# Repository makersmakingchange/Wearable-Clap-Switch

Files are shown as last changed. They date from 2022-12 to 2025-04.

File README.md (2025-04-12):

# Wearable Clap Switch

The Wearable Clap Switch is a wireless assistive switch designed for users that have difficulty using traditional pressure based switches. It consists of a hand mounted transmitter, and a receiver box. When the transmitter detects a clap motion, it sends a signal to the receiver which activates the mono jack. The receiver can be used to activate an 3.5 mm assistive device like a switch adapted toy.

The original version of this project is called the Wearable Bluetooth Controller for Switch Adapted Toys. It was released by [r570sv](https://www.instructables.com/member/r570sv/) on [Instructables](https://www.instructables.com/Wearable-BLE-Controller-for-Switch-Adapted-Toys/) under a [CC-BY-NC-SA license](https://creativecommons.org/licenses/by-nc-sa/4.0/).

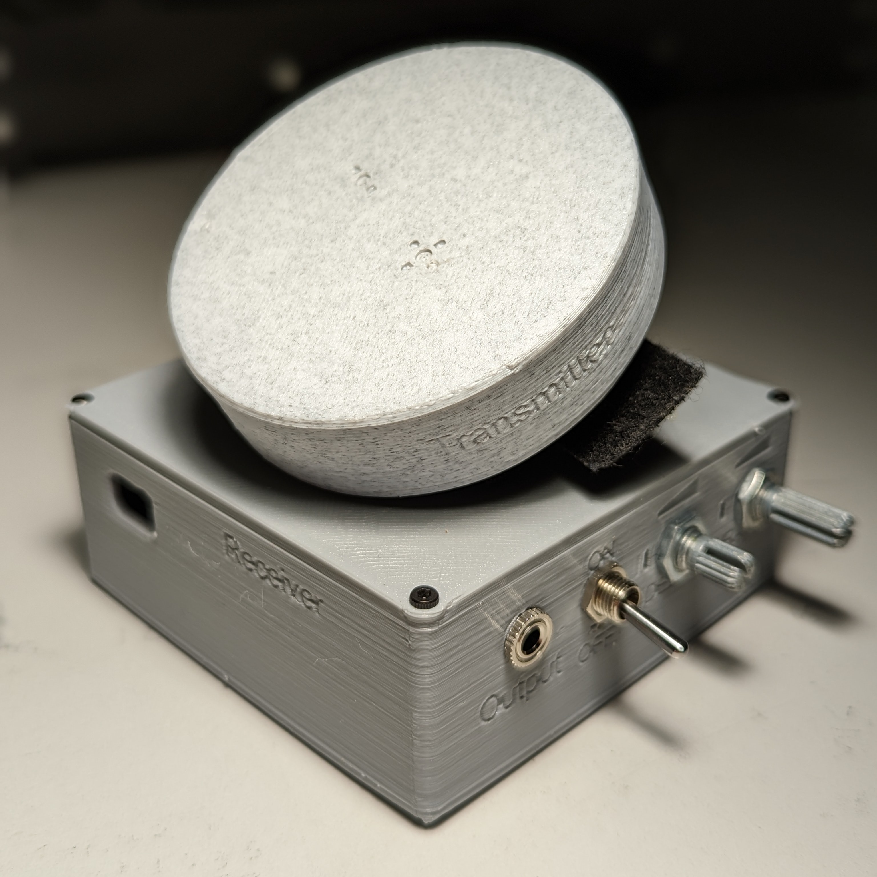
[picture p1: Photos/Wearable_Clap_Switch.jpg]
Picture of Wearable Clap Switch.


## More info at
- [Makers Making Change Project Page](https://makersmakingchange.com/project/wearable-clap-switch)

## How to Obtain a Wearable Clap Switch
### 1. Do it Yourself (DIY) or Do it Together (DIT)

This is an open-source assistive technology, so anyone is free to build it. All of the files and instructions required to build the Wearable Clap Switch are contained within this repository. Refer to the Maker Checklist below.

### 2. Request a build of this device

If you would like to obtain a Wearable Clap Switch , you may submit a build request through the [MMC Library Page](https://makersmakingchange.com/project/wearable-clap-switch/). The requestor is responsible for the cost of materials and any shipping.

### 3. How to build this device for someone else

If you have the skills and equipment to build this device, and would like to donate your time to create the switch for someone who needs it, visit the [MMC Maker Wanted](https://makersmakingchange.com/maker-wanted/) section.

## Getting Started

### 1. Read the Makers Checklist

The Makers Checklist contains all the steps required to build the device for someone.

### 2. Order the Off-The-Shelf Components

The [Bill of Materials](/Documentation/Wearable_Clap_Switch_BOM.xlsx) lists all of the parts and components required to build the Wearable Clap Switch. The main switch component needs to be ordered online. The rest of the off-the-shelf components are also online or may be available in smaller quantities at your local hardware store or dollar store.

### 3. Print the 3D Printable components

Print the components. All of the files and individual print files can be in the [/Build_Files/3D_Printing_Files](/Build_Files/3D_Printing_Files/) folder.

### 4. Assemble the Wearable Clap Switch

Reference the [Assembly Guide](/Documentation/Wearable_Clap_Switch_Assembly_Guide_V1.0.pdf) for the tools and steps required to build each portion.

## Files
### Documentation
| Document             | Version | Link |
|----------------------|---------|------|
| Design Rationale     | 1.0     | [Wearable_Clap_Switch_Design_Rationale](/Documentation/Wearable_Clap_Switch_Design_Rationale_v1.0.pdf)     |
| Maker Checklist      | 1.0     | [Wearable_Clap_Switch_Maker_Checklist](/Documentation/Wearable_Clap_Switch_Maker_Checklist_v1.0.pdf)     |
| Bill of Materials    | 1.0     | [Wearable_Clap_Switch_Bill_of_Materials](/Documentation/Wearable_Clap_Switch_BOM_v1.0.xlsx)     |
| 3D Printing Guide    | 1.0     | [Wearable_Clap_Switch_3D_Printing_Guide](/Documentation/Wearable_Clap_Switch_3D_Printing_Guide_v1.0.pdf)     |
| Assembly Guide       | 1.0     | [Wearable_Clap_Switch_Assembly_Guide](/Documentation/Wearable_Clap_Switch_Assembly_Guide_v1.0.pdf)     |
| User Guide           | 1.0     | [Wearable_Clap_Switch_User_Guide](/Documentation/Wearable_Clap_Switch_User_Guide_v1.0.pdf)    |
| Changelog            | 1.0     | [Wearable_Clap_Switch_Changelog](/Documentation/Wearable_Clap_Switch_Changelog_v1.0.pdf)     |

### Design Files
 - [CAD Files](/Build_Files/Design_Files)

### Build Files
 - [3D Printing Files](/Build_Files/3D_Printing)

### Programming Files
 - [Programming Files](/Code/Current_Code)

## Attribution
The original design of the [Wearable Bluetooth Controller for Switch Adapted Toys](https://www.instructables.com/Wearable-BLE-Controller-for-Switch-Adapted-Toys/) was released by [r570sv](https://www.instructables.com/member/r570sv/) under a [CC-BY-NC-SA license](https://creativecommons.org/licenses/by-nc-sa/4.0/).

Updated 3D Printed Receiver Design, code, and documentation by Brad Wellington / Makers Making Change.

## License
Everything needed or used to design, make, test, or prepare the Wearable Clap Switch is licensed under the [Creative Commons Attribution-NonCommercial-ShareAlike 4.0](https://creativecommons.org/licenses/by-nc-sa/4.0/) . 

Accompanying material such as instruction manuals, videos, and other copyrightable works that are useful but not necessary to design, make, test, or prepare the Wearable Clap Switch are published under a Creative Commons Attribution-ShareAlike 4.0 license https://creativecommons.org/licenses/by-sa/4.0/ (CC BY-SA 4.0).

---
<!-- ABOUT MMC START -->
## About Makers Making Change
[Makers Making Change Logo](https://www.makersmakingchange.com/)

Makers Making Change is a program of [Neil Squire](https://www.neilsquire.ca/), a Canadian non-profit that uses technology, knowledge, and passion to empower people with disabilities.

Makers Making Change leverages the capacity of community based Makers, Disability Professionals and Volunteers to develop and deliver affordable Open Source Assistive Technologies.

 - Website: [www.MakersMakingChange.com](https://www.makersmakingchange.com/)
 - GitHub: [makersmakingchange](https://github.com/makersmakingchange)
 - Bluesky: [@makersmakingchange.bsky.social](https://bsky.app/profile/makersmakingchange.bsky.social)
 - Instagram: [@makersmakingchange](https://www.instagram.com/makersmakingchange)
 - Facebook: [makersmakechange](https://www.facebook.com/makersmakechange)
 - LinkedIn: [Neil Squire Society](https://www.linkedin.com/company/neil-squire-society/)
 - Thingiverse: [makersmakingchange](https://www.thingiverse.com/makersmakingchange/about)
 - Printables: [MakersMakingChange](https://www.printables.com/@MakersMakingChange)

### Contact Us
For technical questions, to get involved, or to share your experience we encourage you to [visit our website](https://www.makersmakingchange.com/) or [contact us](https://www.makersmakingchange.com/s/contact).
<!-- ABOUT MMC END -->

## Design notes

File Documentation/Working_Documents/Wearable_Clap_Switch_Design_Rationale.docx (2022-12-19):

# Introduction

The Wearable Clap Switch is a device that operates a switch when the user claps. It is intended for users that have difficulty operating standard push or squeeze switches.

# Research

Commercial Options
Name | Picture | Price | Link

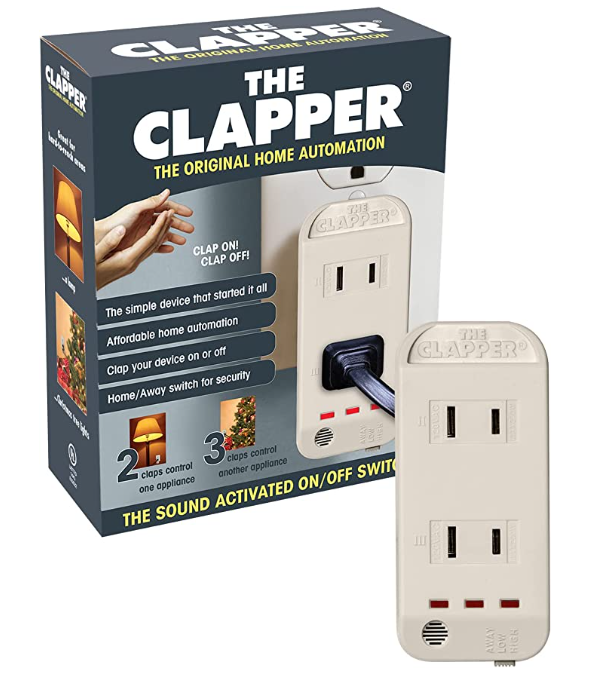
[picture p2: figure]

Clapper Activated Sound Switch | | $39.15 | Link (https://www.amazon.ca/Clapper-Sound-Activated-Switch-Each/dp/B0000CGKLR)

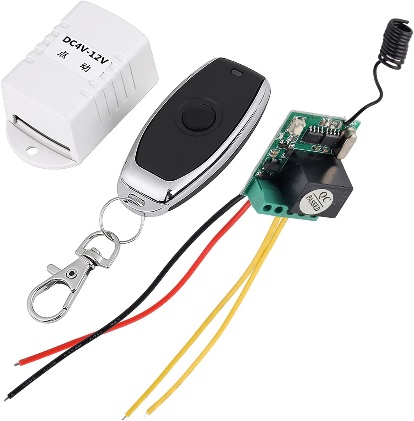
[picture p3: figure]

Wireless Switch Receiver | | $19.02 | Link (https://www.amazon.ca/gp/product/B0762HH45G/ref=ppx_yo_dt_b_asin_title_o01_s00?ie=UTF8&psc=1)

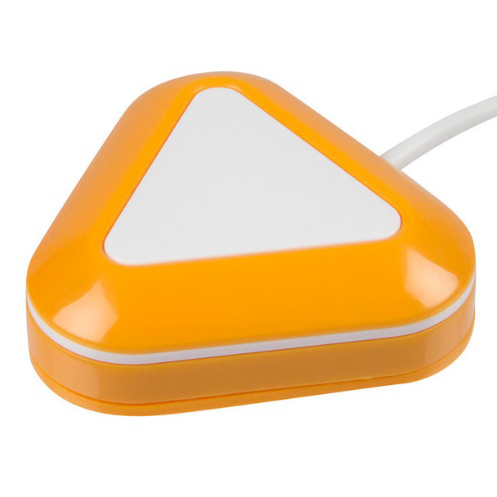
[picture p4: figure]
LITTLE Candy Corn Proximity Switch

Little Candy Corn Proximity Switch | | $310.14 | Link (https://www.adaptivetechsolutions.com/little-candy-corn-proximity-switch/)

DIY Options

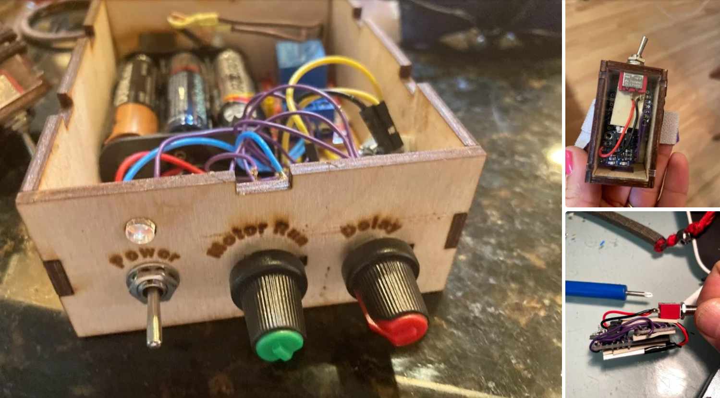
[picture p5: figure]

Wearable Bluetooth Controller for Switch Adapted Toys | | | Link (https://www.instructables.com/Wearable-BLE-Controller-for-Switch-Adapted-Toys/)

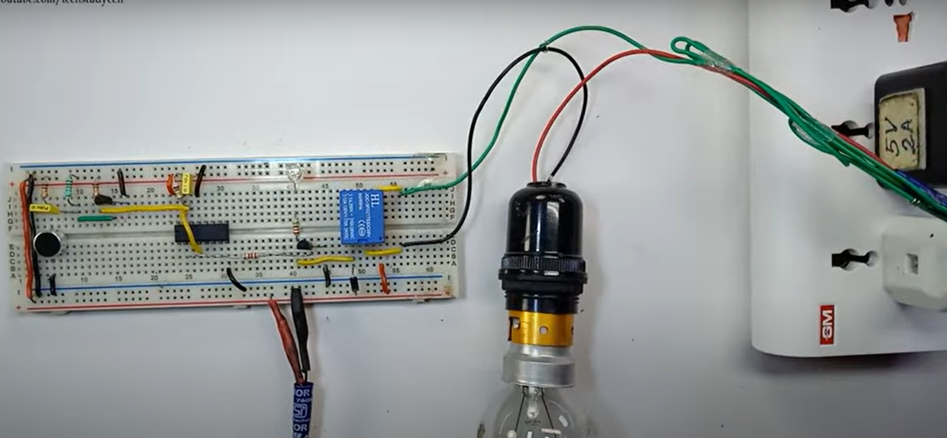
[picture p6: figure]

Simple Clap Circuit for Home Automation | | | Link (https://www.youtube.com/watch?v=KToo8p2EG-4)

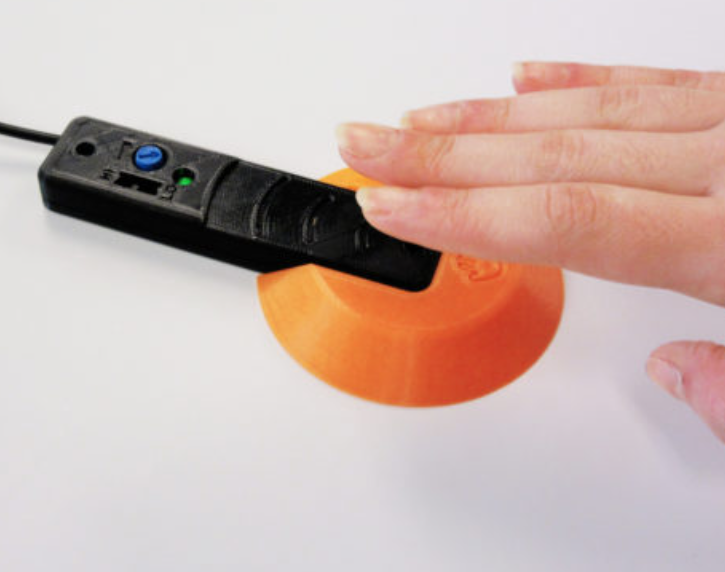
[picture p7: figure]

Light Proximity Switch | | | Link (https://makersmakingchange.com/project/light-proximity-switch/)

# Requirements

## Goals

G01 | Operate a switch when the user claps

## Functional Requirements

F01 | Device must operate a switch when the user claps(or just accelerates their hand?)
F02 | Device must not hinder/obstruct user (e.g. tangle them with wires)
F03 | Device must have adjustable switch delay and duration
F04 | Device must have a 3.5 mm mono output port.
F05 | Device must be chargeable/easy to change batteries.

## Non-functional Requirement

NF01 | All Parts must be off the shelf/3D printable
NF02 | Maker Friendly/Easy to assemble
NF03 | Any handheld/strapped parts of the device must be comfortable enough to wear for long periods of time

## Constraints

C01 | Low-Cost

# Ideation

The idea for this project came from the original instructable project, which designed a clap-based switch for a person who had difficulty interacting with push or squeeze based switches but was very good at clapping.

## User Controllable Parameters

- Duration of the output
- Delay between activations
- Triggering sensitivity (i.e., accelerometer threshold)

## Trigger Method

- Original – acceleration magnitude
- Gesture recognition
- Sounds intensity threshold

# Conceptual Design

## Original Design

This design stays true to the original Instructables design, using two ItsyBitsy nrf52840 microcontrollers, full size potentiometers, and soldered Dupont wires.

The device consists of one handheld unit containing an accelerometer and a Bluetooth microcontroller. When the microcontroller detects movement over a threshold, it sends a signal to the receiver unit. The receiver unit contains another Bluetooth microcontroller, a relay, two input potentiometers, and a 3.5 mm mono jack. When the receiver gets the signal, it activates the relay to close the output jack with a delay and duration set by the input potentiometers.

~$100-$110

### Opportunities for Improvement

- Find alternative relay board to reduce BOM cost

## Concept 2 – Different Microcontroller

This concept is similar to the original design, but switches to Feather microcontrollers. This brings the battery backpacks onto the main board and allows for Featherwing boards to be used to bring the amount of soldering and loose wires to a minimum. There are several relay Featherwings, with both regular and solid state relays, as well as several accelerometer Featherwings.

The device consists of one handheld unit containing an accelerometer and a Bluetooth microcontroller. When the microcontroller detects movement over a threshold, it sends a signal to the receiver unit. The receiver unit contains another Bluetooth microcontroller, a relay, two input potentiometers, and a 3.5 mm mono jack. When the receiver gets the signal, it activates the relay to close the output jack with a delay and duration set by the input potentiometers.

~$130-$140

## Concept 3 – Wireless Relay Switch

This concept uses the same wireless relay switch as the Wireless Assistive Switch Link (https://makersmakingchange.com/project/wireless-assistive-switch-link/) project with a small microcontroller such as the Seed Xiao SAMD21 connected to the accelerometer in the hand mounted enclosure. When the accelerometer detects a movement over the threshold, it signals the transmitter with a duration and delay set by the two input potentiometers on the handheld unit. When the receiver relay gets a signal, it will send a signal to the 3.5 mm mono output port as long as it continues to receive the input signal.

The primary downside of this concept is the fact that the duration and delay potentiometers have to be mounted on the hand section of the device to control the output to the wireless relay switch. This is added weight, but there are small potentiometers that can be used, such as the ones on the OpenAT Toy

~$50-$60

## Concept 4 – Clapper

This concept consists of a base station connected to the switch that monitors for the sound of a clap, and will activate the switch when a clap is picked up by a microphone. The switch is activated with a relay which is connected to a 3.5 mm mono output jack with a delay and duration set by two input potentiometers.

~$35-$45

## Concept 5 – Microcontroller with Integrated Sensor

This design is similar to the original design but swaps the hand mounted microcontroller for a board with an onboard accelerometer, Bluetooth, and battery management such as the Feather nrf52840 Sense or the Circuit Playground Bluefruit. These microcontrollers typically have a microphone on board as well, which would allow for verification of a clap through both acceleration and sound.

The device consists of one handheld unit containing a Bluetooth microcontroller with built in accelerometer and microphone. When the microcontroller detects movement over a threshold and confirms the clap with sound from the microphone, it sends a signal to the receiver unit. The receiver unit contains another Bluetooth microcontroller, a relay, two input potentiometers, and a 3.5 mm mono jack. When the receiver gets the signal, it activates the relay to close the output jack with a delay and duration set by the input potentiometers.

~$100-$110

## Concept Comparison

Criteria/Concept | Original | Concept 2 | Concept 3 | Concept 4 | Concept 5
Function | 7 | 7 | 7 | 6 | 8
Battery Life | N/A | N/A | N/A | N/A | N/A
Size | 4 | 6 | 8 | 7 | 8
Weight | 5 | 6 | 7 | 9 | 7
Price | 7 | 6 | 8 | 9 | 6
Adaptability | 6 | | | | 9
Customizability | 6 | 6 | 4 | 3 | 9
Makeability | 6 | 7 | 6 | 5 | 8
Design Effort | 7 | 7 | 6 | 6 | 7

# Detailed Design

## Power Supply Options

- LiPo Battery Pack
  - ~3.7 V DC
  - No power switch
  - Would need to be able to access the JST connector to charge the battery
  - Difficult to ship
  - ~150 mAh, can increase to up to 2000 mAh with enclosure redesign
  - ~5 to 66.5 h of battery life
  - With very minimal enclosure changes, 350 mAh battery can be installer with ~11.5h battery life
  - Charge rate of 100 mA
- AAA battery pack
  - 3xAAA batteries, ~4.5 V DC
  - Power switch
  - Would need to disassemble to change batteries
  - ~1200 mAh
  - As thick as the current enclosure
  - ~40h of battery life
- Coin cell
  - 2xCR2032 ~6 V DC
  - Power switch
  - Would need to disassemble to change batteries
  - ~235 mAh
  - ~7.5h of battery life

Circuit playground can take up to 6V DC and has reverse polarity, over-current, and thermal protection. The circuit playground consumes around 30 mA of current during operation. (https://blog.adafruit.com/2019/10/25/circuitplayground-bluefruit-low-power-tests-adafruit-bluefruit-arduino-circuitpython/)

## Enclosure Design

### Transmitter

- Lightweight
- Charging port accessible
- No sharp edges

### Receiver

- Charging port accessible
- No sharp edges

# Opportunities for Improvement

Transmitter

- Integrate charging circuit into the enclosure
- Change the communication protocol so the transmitter can be used for more projects, like controlling a remote-control car.
- Stiffen base so it won’t warp if removed from print bed while warm

Receiver

- Add knobs on input potentiometers
- Cover on programming port

© 2022 by Neil Squire. This work is licensed under the CC BY SA 4.0 License: http://creativecommons.org/licenses/by-sa/4.0 Files available at https://makersmakingchange.com/project/wearable-clap-switch/ Page 1 of 2

V1.0 | December 2022 Wearable Clap Switch Design Rationale

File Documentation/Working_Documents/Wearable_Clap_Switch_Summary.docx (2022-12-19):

# Title

Wearable Clap Switch

## Subtitle

The Wearable Clap Switch allows a user to wirelessly activate a switch activated device with a clap.

## Device Details

### Overview

The Wearable Clap Switch is a wireless assistive switch designed for users that have difficulty using traditional pressure based switches. It consists of a hand mounted transmitter, and a receiver box. When the transmitter detects a clap motion, it sends a signal to the receiver which activates the mono jack. The receiver can be used to activate an 3.5 mm assistive device like a switch adapted toy.

The original version of this project is called the Wearable Bluetooth Controller for Switch Adapted Toys. It was released by r570sv (https://www.instructables.com/member/r570sv/) on Instructables (https://www.instructables.com/Wearable-BLE-Controller-for-Switch-Adapted-Toys/) under a CC-BY-NC-SA (https://creativecommons.org/licenses/by-nc-sa/4.0/) license.

### Usage

When a clap motion is detected by the hand-mounted transmitter, the receiver will activate the connected assistive device.

Transmitter

Attach the transmitter to the users hand or wrist using the strap.

To activate the transmitter, slide the switch on the bottom of the transmitter. The transmitter will start looking for a connection, and if a receiver is broadcasting, the two will connect. Once the two have connected, the transmitter will send a signal to the receiver whenever it detects a clap.

The sensitivity of the clap detection can be adjusted using the two buttons on the top of the case. Pressing the increase sensitivity button will cause the number of illuminated LEDs in the circle to increase. Pressing the decrease sensitivity button will cause the number of illuminated LEDs in the circle to decrease.

Receiver

Connect the assistive device to the output port on the receiver using a 3.5 mm cable.

To active the receiver, flip the toggle switch from off to on. The receiver will start looking for a connection, and if the transmitter is broadcasting, the two will connect. Once they have connected, the receiver will power a relay to activate the mono jack.

To change how long the jack stays activated, adjust the potentiometer labeled Duration. To change the cooldown between activations, adjust the potentiometer labeled Delay.

### Cost

~$110

### Build Instructions

The transmitter is assembled with mostly off the shelf parts, the only addition being the soldering of a power switch onto the battery line. All the shell and other mechanical components are 3D printed. For the receiver, there is medium soldering to assemble the protoboard

#### Skills Required

- 3D Printing
- Soldering

#### Time Required

- 3D Print Time: 12h 8min
- Assembly Time: 1h

#### Tools

- 3D printer
- Soldering iron
- Hobby knife
- Multimeter
- Flush cutters
- Flux

#### Components

- 1X Transmitter
- 1X Receiver

#### 3D Printing

All components can be printed with no support at 20% infill with a 0.2mm layer height. All pieces can be printed using PLA filament Programming

### Attribution

The original design of the Wearable Bluetooth Controller for Switch Adapted Toys (https://www.instructables.com/Wearable-BLE-Controller-for-Switch-Adapted-Toys/) was released by r570sv (https://www.instructables.com/member/r570sv/) under a CC-BY-NC-SA (https://creativecommons.org/licenses/by-nc-sa/4.0/) license.

Updated 3D Printed Receiver Design, code, and documentation by Brad Wellington / Makers Making Change.

© 2022 by Neil Squire. This work is licensed under the CC BY SA 4.0 License: http://creativecommons.org/licenses/by-sa/4.0 Files available at https://makersmakingchange.com/project/wearable-clap-switch/ Page 2 of 3

V1.0 | December 2022 Wearable Clap Switch Summary

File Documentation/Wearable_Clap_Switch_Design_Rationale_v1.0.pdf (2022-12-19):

V1.0 | December 2022

## Wearable Clap Switch

## DESIGN RATIONALE

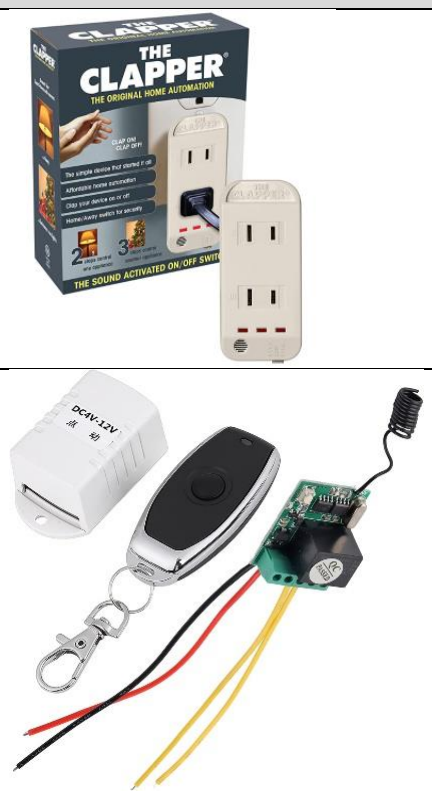
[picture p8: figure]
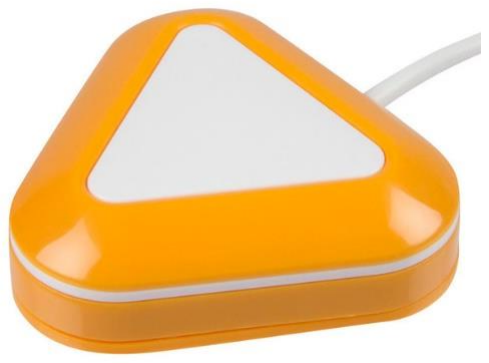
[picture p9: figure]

© 2022 by Neil Squire. (https://neilsquire.ca/)
This work is licensed under the CC BY SA 4.0 License: http://creativecommons.org/licenses/by-sa/4.0
Files available at https://makersmakingchange.com/project/wearable-clap-switch/ (https://makersmakingchange.com/?post_type=project&p=20045&preview=true) | Page 1 of 7

### Introduction

The Wearable Clap Switch is a device that operates a switch when the user claps. It is intended for users that have difficulty operating standard push or squeeze switches.

### Research

Commercial Options
Name | Picture | Price | Link
Clapper Activated Sound Switch | | $39.15 | Link (https://www.amazon.ca/Clapper-Sound-Activated-Switch-Each/dp/B0000CGKLR)
Wireless Switch Receiver | | $19.02 | Link (https://www.amazon.ca/gp/product/B0762HH45G/ref=ppx_yo_dt_b_asin_title_o01_s00?ie=UTF8&psc=1)
Little Candy Corn Proximity Switch | | $310.14 | Link (https://www.adaptivetechsolutions.com/little-candy-corn-proximity-switch/)

## DESIGN RATIONALE

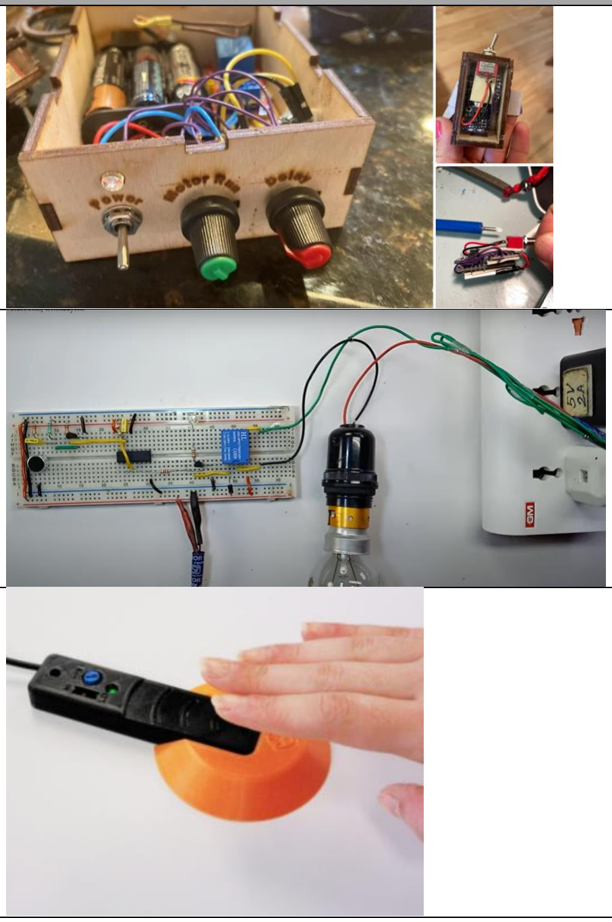
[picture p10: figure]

Files available at https://makersmakingchange.com/project/wearable-clap-switch/ (https://makersmakingchange.com/?post_type=project&p=20045&preview=true) | Page 2 of 7

DIY Options
Wearable Bluetooth Controller for Switch Adapted Toys | Link (https://www.instructables.com/Wearable-BLE-Controller-for-Switch-Adapted-Toys/)
Simple Clap Circuit for Home Automation | Link (https://www.youtube.com/watch?v=KToo8p2EG-4)
Light Proximity Switch | Link (https://makersmakingchange.com/project/light-proximity-switch/)

### Requirements

### Goals

G01 Operate a switch when the user claps

### Functional Requirements

F01 | Device must operate a switch when the user claps(or just accelerates their hand?)
F02 | Device must not hinder/obstruct user (e.g. tangle them with wires)

## DESIGN RATIONALE

Files available at https://makersmakingchange.com/project/wearable-clap-switch/ (https://makersmakingchange.com/?post_type=project&p=20045&preview=true) | Page 3 of 7
F03 | Device must have adjustable switch delay and duration
F04 | Device must have a 3.5 mm mono output port.
F05 | Device must be chargeable/easy to change batteries.

### Non-functional Requirement

NF01 | All Parts must be off the shelf/3D printable
NF02 | Maker Friendly/Easy to assemble
NF03 | Any handheld/strapped parts of the device must be comfortable enough to wear for long periods of time

### Constraints

C01 Low-Cost

### Ideation

The idea for this project came from the original instructable project, which designed a clap-based switch for a person who had difficulty interacting with push or squeeze based switches but was very good at clapping.

### User Controllable Parameters

- Duration of the output
- Delay between activations
- Triggering sensitivity (i.e., accelerometer threshold)

### Trigger Method

- Original – acceleration magnitude
- Gesture recognition
- Sounds intensity threshold

### Conceptual Design

### Original Design

This design stays true to the original Instructables design, using two ItsyBitsy nrf52840 microcontrollers, full size potentiometers, and soldered Dupont wires.

## DESIGN RATIONALE

Files available at https://makersmakingchange.com/project/wearable-clap-switch/ (https://makersmakingchange.com/?post_type=project&p=20045&preview=true) | Page 4 of 7

The device consists of one handheld unit containing an accelerometer and a Bluetooth microcontroller. When the microcontroller detects movement over a threshold, it sends a signal to the receiver unit. The receiver unit contains another Bluetooth microcontroller, a relay, two input potentiometers, and a 3.5 mm mono jack. When the receiver gets the signal, it activates the relay to close the output jack with a delay and duration set by the input potentiometers.

~$100-$110

Opportunities for Improvement
- Find alternative relay board to reduce BOM cost

### Concept 2 – Different Microcontroller

This concept is similar to the original design, but switches to Feather microcontrollers. This brings the battery backpacks onto the main board and allows for Featherwing boards to be used to bring the amount of soldering and loose wires to a minimum. There are several relay Featherwings, with both regular and solid state relays, as well as several accelerometer Featherwings.

The device consists of one handheld unit containing an accelerometer and a Bluetooth microcontroller. When the microcontroller detects movement over a threshold, it sends a signal to the receiver unit. The receiver unit contains another Bluetooth microcontroller, a relay, two input potentiometers, and a 3.5 mm mono jack. When the receiver gets the signal, it activates the relay to close the output jack with a delay and duration set by the input potentiometers.

~$130-$140

### Concept 3 – Wireless Relay Switch

This concept uses the same wireless relay switch as the Wireless Assistive Switch Link (https://makersmakingchange.com/project/wireless-assistive-switch-link/) project with a small microcontroller such as the Seed Xiao SAMD21 connected to the accelerometer in the hand mounted enclosure. When the accelerometer detects a movement over the threshold, it signals the transmitter with a duration and delay set by the two input potentiometers on the handheld unit. When the receiver relay gets a signal, it will send a signal to the 3.5 mm mono output port as long as it continues to receive the input signal.

The primary downside of this concept is the fact that the duration and delay potentiometers have to be mounted on the hand section of the device to control the output to the wireless relay switch. This is added weight, but there are small potentiometers that can be used, such as the ones on the OpenAT Toy

~$50-$60

## DESIGN RATIONALE

Files available at https://makersmakingchange.com/project/wearable-clap-switch/ (https://makersmakingchange.com/?post_type=project&p=20045&preview=true) | Page 5 of 7

### Concept 4 – Clapper

This concept consists of a base station connected to the switch that monitors for the sound of a clap, and will activate the switch when a clap is picked up by a microphone. The switch is activated with a relay which is connected to a 3.5 mm mono output jack with a delay and duration set by two input potentiometers.

~$35-$45

### Concept 5 – Microcontroller with Integrated Sensor

This design is similar to the original design but swaps the hand mounted microcontroller for a board with an onboard accelerometer, Bluetooth, and battery management such as the Feather nrf52840 Sense or the Circuit Playground Bluefruit. These microcontrollers typically have a microphone on board as well, which would allow for verification of a clap through both acceleration and sound.

The device consists of one handheld unit containing a Bluetooth microcontroller with built in accelerometer and microphone. When the microcontroller detects movement over a threshold and confirms the clap with sound from the microphone, it sends a signal to the receiver unit. The receiver unit contains another Bluetooth microcontroller, a relay, two input potentiometers, and a 3.5 mm mono jack. When the receiver gets the signal, it activates the relay to close the output jack with a delay and duration set by the input potentiometers.

~$100-$110

### Concept Comparison

Criteria/Concept | Original | Concept 2 | Concept 3 | Concept 4 | Concept 5
Function | 7 | 7 | 7 | 6 | 8
Battery Life
Size | 4 | 6 | 8 | 7 | 8
Weight | 5 | 6 | 7 | 9 | 7
Price | 7 | 6 | 8 | 9 | 6
Adaptability | 6 | | | | 9
Customizability | 6 | 6 | 4 | 3 | 9
Makeability | 6 | 7 | 6 | 5 | 8
Design Effort | 7 | 7 | 6 | 6 | 7

## DESIGN RATIONALE

Files available at https://makersmakingchange.com/project/wearable-clap-switch/ (https://makersmakingchange.com/?post_type=project&p=20045&preview=true) | Page 6 of 7

### Detailed Design

### Power Supply Options

- LiPo Battery Pack
- ~3.7 V DC
- No power switch
- Would need to be able to access the JST connector to charge the battery
- Difficult to ship
- ~150 mAh, can increase to up to 2000 mAh with enclosure redesign
- ~5 to 66.5 h of battery life
- With very minimal enclosure changes, 350 mAh battery can be installer with ~11.5h battery life
- Charge rate of 100 mA
- AAA battery pack
- 3xAAA batteries, ~4.5 V DC
- Power switch
- Would need to disassemble to change batteries
- ~1200 mAh
- As thick as the current enclosure
- ~40h of battery life
- Coin cell
- 2xCR2032 ~6 V DC
- Power switch
- Would need to disassemble to change batteries
- ~235 mAh
- ~7.5h of battery life

Circuit playground can take up to 6V DC and has reverse polarity, over-current, and thermal protection. The circuit playground consumes around 30 mA of current during operation. (https://blog.adafruit.com/2019/10/25/circuitplayground-bluefruit-low-power-tests-adafruit-bluefruit-arduino-circuitpython/)

### Enclosure Design

Transmitter
- Lightweight
- Charging port accessible
- No sharp edges

Receiver
- Charging port accessible
- No sharp edges

## DESIGN RATIONALE

Files available at https://makersmakingchange.com/project/wearable-clap-switch/ (https://makersmakingchange.com/?post_type=project&p=20045&preview=true) | Page 7 of 7

### Opportunities for Improvement

Transmitter

- Integrate charging circuit into the enclosure
- Change the communication protocol so the transmitter can be used for more projects, like controlling a remote-control car.
- Stiffen base so it won’t warp if removed from print bed while warm

Receiver

- Add knobs on input potentiometers
- Cover on programming port

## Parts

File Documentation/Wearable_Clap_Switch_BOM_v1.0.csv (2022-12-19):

Wearable Clap Switch |  | Total Cost | Total Print time (hr) | Total filament (g)
Version: V1.0 | Date Created: 10/18/2022 | $113.35 | 11.80 | 89.5
Commercial Parts:
Part type (Electrical. Mechanical, Sanitization, etc) | Part Name | Quantity Needed | Pkg Quantity | Price per package | Price per Unit | Price for qty needed | Link
Electrical | Circuit Playground Bluefruit | 1 | 1 | $39.31 | $39.31 | $39.31 | https://www.digikey.ca/en/products/detail/adafruit-industries-llc/4333/11201431
Electrical | ItsyBitsy nrf52840 Express | 1 | 1 | $27.46 | $27.46 | $27.46 | https://www.adafruit.com/product/4481
Electrical | Battery backpack | 1 | 1 | $6.81 | $6.81 | $6.81 | https://www.adafruit.com/product/2124
Electrical | 150 mAh LiPo Battery | 2 | 1 | $8.19 | $8.19 | $16.38 | https://www.adafruit.com/product/1317
Electrical | 10kOhm Potentiometer | 2 | 1 | $1.31 | $1.31 | $2.62 | https://www.adafruit.com/product/562
Electrical | Mini Toggle Switch | 2 | 1 | $1.31 | $1.31 | $2.62 | https://www.adafruit.com/product/3221
Electrical | Protoboard | 1 | 50 | $19.99 | $0.40 | $0.40 | https://www.amazon.ca/gp/product/B07F7WBY7Y/ref=ppx_yo_dt_b_asin_title_o02_s01?ie=UTF8&psc=1
Electrical | Slide switch | 1 | 1 | $2.75 | $2.75 | $2.75 | https://www.digikey.ca/en/products/detail/nkk-switches/ss12sdp2/1014829
Electrical | LiPo Charge Circuit | 1 | 1 | $10.23 | $10.23 | $10.23 | https://www.digikey.ca/en/products/detail/adafruit-industries-llc/1904/5054545
Electrical | 3.5 mm mono jack | 1 | 1 | $2.53 | $2.53 | $2.53 | https://www.digikey.ca/en/products/detail/switchcraft-inc/35RAPC2AV/772080
3D Printed Parts ESTIMATED PRICING USING 1KG ROLL COST: | $25.00
Part | Description | Quantity Needed | TOTAL Mass (g) | Estimated Price | Print Time (Min) | Link
Transmitter_Lid.stl | Transmitter Lid | 1 | 16 | $0.40 | 149
Transmitter_Base.stl | Transmitter Base | 1 | 9 | $0.23 | 78
Receiver_Lid.stl | Receiver Lid | 1 | 20 | $0.50 | 132
Receiver_Base.stl | Receiver Base | 1 | 44 | $1.10 | 347
Transmitter_Cover.stl | Transmitter Sliding Cover | 2 | 0.5 | $0.01 | 2
Transmitter_Button.stl | Transmitter Button | 2 | 0.2 | $0.01 | 9
 |  |  | Total Print Cost: | $2.24
Tools for Assembly
Soldering Iron
Alternatives (if there are other sources for some parts link them below)
Part and description | Link

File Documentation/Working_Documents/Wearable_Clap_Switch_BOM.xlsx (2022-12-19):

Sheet: Final BOM
Wearable Clap Switch |  | Total Cost | Total Print time (hr) | Total filament (g)
Version: V1.0 | Date Created: 10/18/2022 | $113.35 | 11.80 | 89.5
Commercial Parts:
Part type (Electrical. Mechanical, Sanitization, etc) | Part Name | Quantity Needed | Pkg Quantity | Price per package | Price per Unit | Price for qty needed | Link
Electrical | Circuit Playground Bluefruit | 1 | 1 | $39.31 | $39.31 | $39.31 | https://www.digikey.ca/en/products/detail/adafruit-industries-llc/4333/11201431
Electrical | ItsyBitsy nrf52840 Express | 1 | 1 | $27.46 | $27.46 | $27.46 | https://www.adafruit.com/product/4481
Electrical | Battery backpack | 1 | 1 | $6.81 | $6.81 | $6.81 | https://www.adafruit.com/product/2124
Electrical | 150 mAh LiPo Battery | 2 | 1 | $8.19 | $8.19 | $16.38 | https://www.adafruit.com/product/1317
Electrical | 10kOhm Potentiometer | 2 | 1 | $1.31 | $1.31 | $2.62 | https://www.adafruit.com/product/562
Electrical | Mini Toggle Switch | 2 | 1 | $1.31 | $1.31 | $2.62 | https://www.adafruit.com/product/3221
Electrical | Protoboard | 1 | 50 | $19.99 | $0.40 | $0.40 | https://www.amazon.ca/gp/product/B07F7WBY7Y/ref=ppx_yo_dt_b_asin_title_o02_s01?ie=UTF8&psc=1
Electrical | Slide switch | 1 | 1 | $2.75 | $2.75 | $2.75 | https://www.digikey.ca/en/products/detail/nkk-switches/ss12sdp2/1014829
Electrical | LiPo Charge Circuit | 1 | 1 | $10.23 | $10.23 | $10.23 | https://www.digikey.ca/en/products/detail/adafruit-industries-llc/1904/5054545
Electrical | 3.5 mm mono jack | 1 | 1 | $2.53 | $2.53 | $2.53 | https://www.digikey.ca/en/products/detail/switchcraft-inc/35RAPC2AV/772080
3D Printed Parts ESTIMATED PRICING USING 1KG ROLL COST: | $25.00
Part | Description | Quantity Needed | TOTAL Mass (g) | Estimated Price | Print Time (Min) | Link
Transmitter_Lid.stl | Transmitter Lid | 1 | 16 | $0.40 | 149
Transmitter_Base.stl | Transmitter Base | 1 | 9 | $0.22 | 78
Receiver_Lid.stl | Receiver Lid | 1 | 20 | $0.50 | 132
Receiver_Base.stl | Receiver Base | 1 | 44 | $1.10 | 347
Transmitter_Cover.stl | Transmitter Sliding Cover | 2 | 0.5 | $0.01 | 2
Transmitter_Button.stl | Transmitter Button | 2 | 0.2 | $0.01 | 9
 |  |  | Total Print Cost: | $2.24
Tools for Assembly
Soldering Iron
Alternatives (if there are other sources for some parts link them below)
Part and description | Link

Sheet: BOM Concept 1
Device: Wearable Bluetooth Controller |  | Total Cost | Total Print time (hr) | Total filament (g)
Version: V1.0 | Date Created: 10/18/2022 | $100.62 | 0.00 | 0
Commercial Parts:
Part type (Electrical. Mechanical, Sanitization, ect) | Part Name | Quantity Needed | Pkg Quantity | Price per package | Price per Unit | Price for qty needed | Link
Electrical | ItsyBitsy nrf52840 Express | 2 | 1 | $27.46 | $27.46 | $54.92 | https://www.adafruit.com/product/4481
Electrical | Battery Backpack | 1 | 1 | $6.81 | $6.81 | $6.81 | https://www.adafruit.com/product/2124
Electrical | Triple Axis Accelerometer | 1 | 1 | $10.94 | $10.94 | $10.94 | https://www.adafruit.com/product/2019
Electrical | 150 mAh LiPo Battery | 2 | 1 | $8.19 | $8.19 | $16.38 | https://www.adafruit.com/product/1317
Electrical | 10K Ohm Potentiometer | 2 | 1 | $1.31 | $1.31 | $2.62 | https://www.adafruit.com/product/3221
Electrical | 3.5 mm mono jack | 1 | 1 | $2.53 | $2.53 | $2.53 | https://www.digikey.ca/en/products/detail/switchcraft-inc/35RAPC2AV/772080
Electrical | Mini Toggle Switch | 2 | 1 | $1.31 | $1.31 | $2.62 | https://www.adafruit.com/product/3221
Electrical | 5V Relay | 1 | 5 | $18.99 | $3.80 | $3.80 | https://www.amazon.ca/gp/product/B07DN8WTKX/ref=ppx_yo_dt_b_asin_title_o01_s00?ie=UTF8&psc=1
3D Printed Parts ESTIMATED PRICING USING 1KG ROLL COST: | $25.00
Part | Description | Quantity Needed | TOTAL Mass (g) | Estimated Price | Print Time (Min) | Link
 |  |  |  | $0.00
 |  |  |  | $0.00
 |  |  |  | $0.00
 |  |  |  | $0.00
 |  |  |  | $0.00
 |  |  | Total Print Cost: | $0.00
Tools for Assembly
Soldering Iron
Alternatives (if there are other sources for some parts link them below)
Part and description | Link

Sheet: BOM Concept 2
Device: Wearable Bluetooth Controller |  | Total Cost | Total Print time (hr) | Total filament (g)
Version: V1.0 | Date Created: 10/18/2022 | $132.21 | 0.00 | 0
Commercial Parts:
Part type (Electrical. Mechanical, Sanitization, ect) | Part Name | Quantity Needed | Pkg Quantity | Price per package | Price per Unit | Price for qty needed |  | Link
Electrical | Feather nrf52840 Express | 2 | 1 | $39.31 | $39.31 | $78.62 |  | https://www.digikey.ca/en/products/detail/adafruit-industries-llc/4062/9843410
Electrical | Accelerometer featherwing | 1 | 1 | $17.68 | $17.68 | $17.68 |  | https://www.digikey.ca/en/products/detail/adafruit-industries-llc/4147/9955494
Electrical | 150mAh LiPo Battery | 2 | 1 | $8.19 | $8.19 | $16.38 |  | https://www.adafruit.com/product/1317
Electrical | 10kOhm Potentiometer | 2 | 1 | $1.31 | $1.31 | $2.62 |  | adafruit.com/product/562
Electrical | Mini Toggle Switch | 2 | 1 | $1.31 | $1.31 | $2.62 |  | https://www.adafruit.com/product/3221
Electrical | 3.5 mm mono jack | 1 | 1 | $2.53 | $2.53 | $2.53 | https://www.digikey.ca/en/products/detail/switchcraft-inc/35RAPC2AV/772080
 | Non Latching Relay Featherwing | 1 | 1 | $11.76 | $11.76 | $11.76 |  | https://www.digikey.ca/en/products/detail/adafruit-industries-llc/2895/5979891
3D Printed Parts ESTIMATED PRICING USING 1KG ROLL COST: | $25.00
Part | Description | Quantity Needed | TOTAL Mass (g) | Estimated Price | Print Time (Min) | Link
 |  |  |  | $0.00
 |  |  |  | $0.00
 |  |  |  | $0.00
 |  |  |  | $0.00
 |  |  |  | $0.00
 |  |  | Total Print Cost: | $0.00
Tools for Assembly
Soldering Iron
Alternatives (if there are other sources for some parts link them below)
Part and description | Link

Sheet: BOM Concept 3
Wearable Bluetooth Controller |  | Total Cost | Total Print time (hr) | Total filament (g)
Version: V1.0 | Date Created: 10/18/2022 | $52.42 | 0.00 | 0
Commercial Parts:
Part type (Electrical. Mechanical, Sanitization, ect) | Part Name | Quantity Needed | Pkg Quantity | Price per package | Price per Unit | Price for qty needed |  | Link
Electrical | SEEEDuino Xiao | 1 | 1 | $6.50 | $6.50 | $6.50 | https://www.digikey.ca/en/products/detail/seeed-technology-co-ltd/102010388/13572076
Electrical | Wireless switch and reciever | 1 | 1 | $19.02 | $19.02 | $19.02 | https://www.amazon.ca/gp/product/B0762HH45G/ref=ppx_yo_dt_b_asin_title_o01_s00?ie=UTF8&psc=1
Electrical | Triple Axis Accelerometer | 1 | 1 | $10.94 | $10.94 | $10.94 | https://www.adafruit.com/product/2019
Electrical | 150mAh LiPo Battery | 1 | 1 | $8.19 | $8.19 | $8.19 | https://www.adafruit.com/product/1317
Electrical | 10kOhm Potentiometer | 2 | 1 | $1.31 | $1.31 | $2.62 | https://www.adafruit.com/product/3221
Electrical | Mini Toggle Switch | 2 | 1 | $1.31 | $1.31 | $2.62 | https://www.adafruit.com/product/3221
Electrical | 3.5 mm mono jack | 1 | 1 | $2.53 | $2.53 | $2.53 | https://www.digikey.ca/en/products/detail/switchcraft-inc/35RAPC2AV/772080
3D Printed Parts ESTIMATED PRICING USING 1KG ROLL COST: | $25.00
Part | Description | Quantity Needed | TOTAL Mass (g) | Estimated Price | Print Time (Min) | Link
 |  |  |  | $0.00
 |  |  |  | $0.00
 |  |  |  | $0.00
 |  |  |  | $0.00
 |  |  |  | $0.00
 |  |  | Total Print Cost: | $0.00
Tools for Assembly
Soldering Iron
Alternatives (if there are other sources for some parts link them below)
Part and description | Link

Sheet: BOM Concept 4
Device: Wearable Bluetooth Controller |  | Total Cost | Total Print time (hr) | Total filament (g)
Version: V1.0 | Date Created: 10/18/2022 | $41.33 | 0.00 | 0
Commercial Parts:
Part type (Electrical. Mechanical, Sanitization, ect) | Part Name | Quantity Needed | Pkg Quantity | Price per package | Price per Unit | Price for qty needed |  | Link
Electrical | SEEEDuino Xiao | 1 | 1 | $6.50 | $6.50 | $6.50 | https://www.digikey.ca/en/products/detail/seeed-technology-co-ltd/102010388/13572076
Electrical | Battery Backpack | 1 | 1 | $6.81 | $6.81 | $6.81
Electrical | Electret Microphone | 1 | 1 | $9.57 | $9.57 | $9.57 | https://www.adafruit.com/product/1063
Electrical | 150mAh LiPo Battery | 1 | 1 | $8.19 | $8.19 | $8.19 | https://www.adafruit.com/product/1317
Electrical | 10kOhm Potentiometer | 2 | 1 | $1.31 | $1.31 | $2.62 | https://www.adafruit.com/product/3221
Electrical | Mini Toggle Switch | 1 | 1 | $1.31 | $1.31 | $1.31 | https://www.adafruit.com/product/3221
Electrical | 5V Relay | 1 | 5 | $18.99 | $3.80 | $3.80 | https://www.amazon.ca/gp/product/B07DN8WTKX/ref=ppx_yo_dt_b_asin_title_o01_s00?ie=UTF8&psc=1
Electrical | 3.5 mm mono jack | 1 | 1 | $2.53 | $2.53 | $2.53 | https://www.digikey.ca/en/products/detail/switchcraft-inc/35RAPC2AV/772080
3D Printed Parts ESTIMATED PRICING USING 1KG ROLL COST: | $25.00
Part | Description | Quantity Needed | TOTAL Mass (g) | Estimated Price | Print Time (Min) | Link
 |  |  |  | $0.00
 |  |  |  | $0.00
 |  |  |  | $0.00
 |  |  |  | $0.00
 |  |  |  | $0.00
 |  |  | Total Print Cost: | $0.00
Tools for Assembly
Soldering Iron
Alternatives (if there are other sources for some parts link them below)
Part and description | Link

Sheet: BOM Concept 5
Device: Wearable Bluetooth Controller |  | Total Cost | Total Print time (hr) | Total filament (g)
Version: V1.0 | Date Created: 10/18/2022 | $102.77 | 0.00 | 0
Commercial Parts:
Part type (Electrical. Mechanical, Sanitization, ect) | Part Name | Quantity Needed | Pkg Quantity | Price per package | Price per Unit | Price for qty needed |  | Link
Electrical | Circuit Playground Bluefruit | 1 | 1 | $39.31 | $39.31 | $39.31 |  | https://www.digikey.ca/en/products/detail/adafruit-industries-llc/4333/11201431
Electrical | Feather nrf52840 Express | 1 | 1 | $39.31 | $39.31 | $39.31 |  | https://www.digikey.ca/en/products/detail/adafruit-industries-llc/4062/9843410
Electrical | 150mAh LiPo Battery | 2 | 1 | $8.19 | $8.19 | $16.38 |  | https://www.adafruit.com/product/1317
Electrical | 10kOhm Potentiometer | 2 | 1 | $1.31 | $1.31 | $2.62 |  | adafruit.com/product/562
Electrical | Mini Toggle Switch | 2 | 1 | $1.31 | $1.31 | $2.62 |  | https://www.adafruit.com/product/3221
Electrical | 3.5 mm mono jack | 1 | 1 | $2.53 | $2.53 | $2.53 | https://www.digikey.ca/en/products/detail/switchcraft-inc/35RAPC2AV/772080
3D Printed Parts ESTIMATED PRICING USING 1KG ROLL COST: | $25.00
Part | Description | Quantity Needed | TOTAL Mass (g) | Estimated Price | Print Time (Min) | Link
 |  |  |  | $0.00
 |  |  |  | $0.00
 |  |  |  | $0.00
 |  |  |  | $0.00
 |  |  |  | $0.00
 |  |  | Total Print Cost: | $0.00
Tools for Assembly
Soldering Iron
Alternatives (if there are other sources for some parts link them below)
Part and description | Link

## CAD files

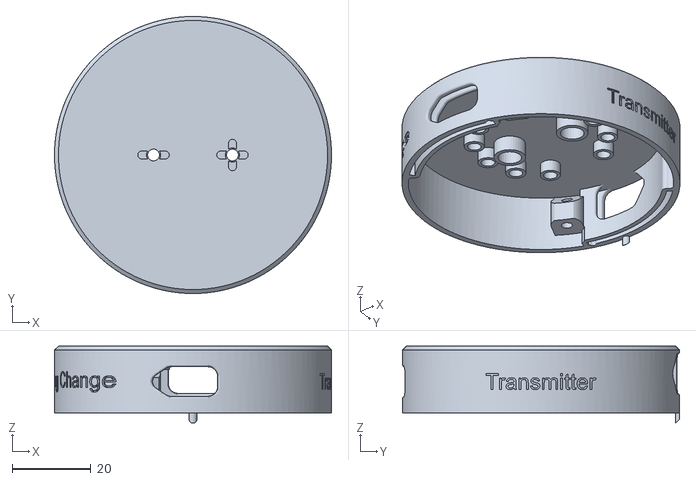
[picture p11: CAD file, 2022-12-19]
Build_Files/3D_Printing_Files/Transmitter Lid.stl
70.2 x 70.2 x 19.5

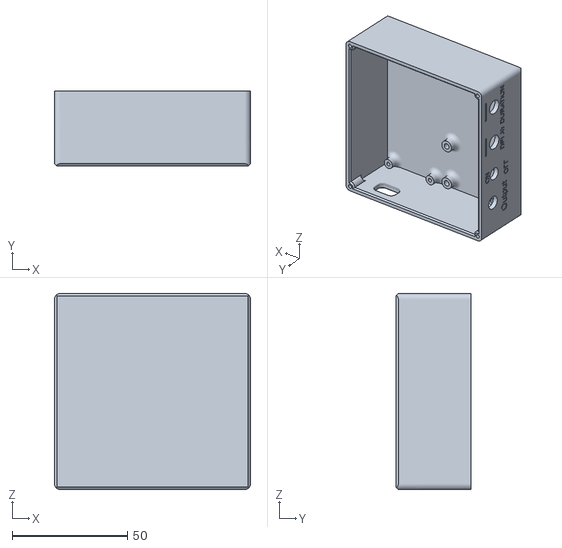
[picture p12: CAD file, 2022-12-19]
Build_Files/3D_Printing_Files/Reciever Base.stl
85.0 x 32.5 x 85.0

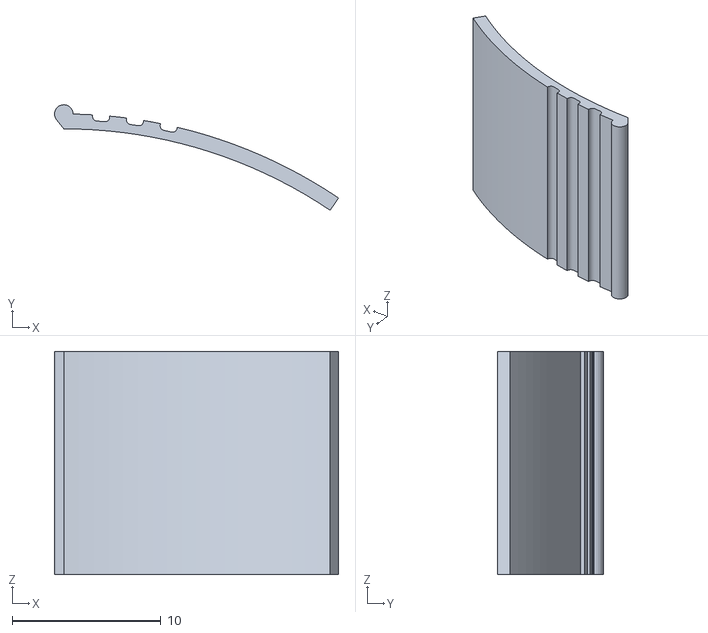
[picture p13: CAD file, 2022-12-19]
Build_Files/3D_Printing_Files/Transmitter Cover.stl
19.1 x 7.10 x 15.0

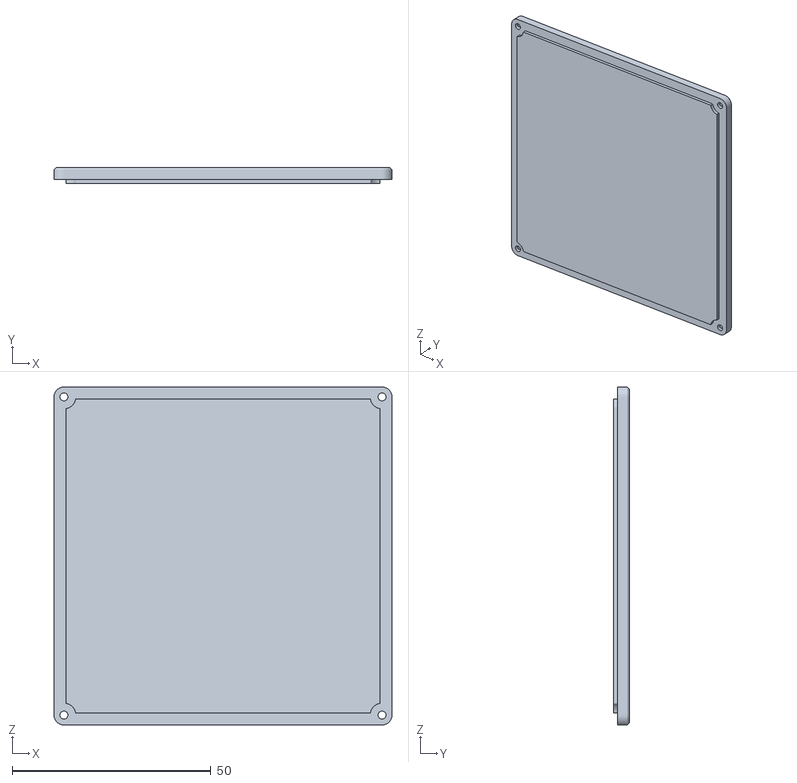
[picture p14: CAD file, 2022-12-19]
Build_Files/3D_Printing_Files/Receiver Lid.stl
85.0 x 4.00 x 85.0

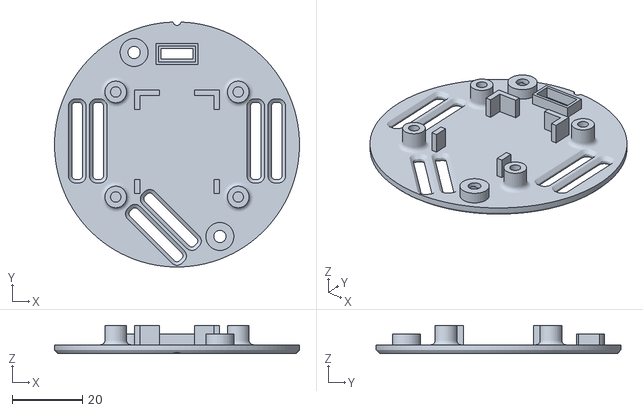
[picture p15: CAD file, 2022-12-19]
Build_Files/3D_Printing_Files/Transmitter Base.stl
70.0 x 70.0 x 8.00

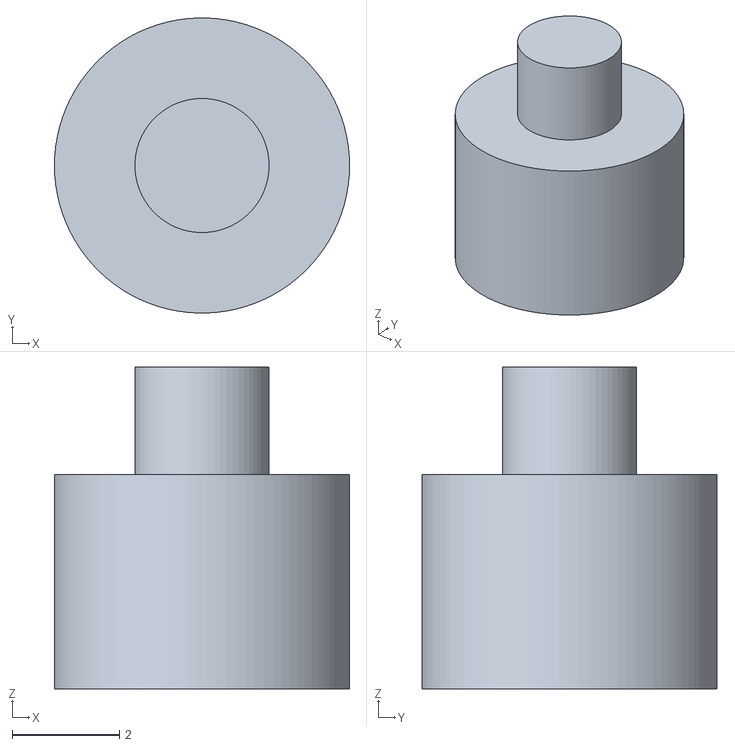
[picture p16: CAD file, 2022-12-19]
Build_Files/3D_Printing_Files/Transmitter Button.stl
5.50 x 5.50 x 6.00

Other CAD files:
Design_Files/Receiver.f3d

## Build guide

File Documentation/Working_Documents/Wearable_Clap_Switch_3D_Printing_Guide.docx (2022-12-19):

# 3D Printing Summary

Metrics | *Configuration 1*
Total Print Time (hr:min) | 12:08
Total Number of Components | 8
Typical Total Mass (g) | 90
Typical Number of Print Setups | 5

# 3D Printing Settings

Print File Name | Qty | Total Print Time (hr:min) | Mass (g) | Infill (%) | Support(Y/N) | Layer Height/ Nozzle Diameter(mm) | Notes (orientation, special settings, etc.)
Transmitter_Lid.stl | 1 | 2:29 | 16 | 20 | N | 0.2/0.4 | - Print in orientation given in STL
Transmitter_Base.stl | 1 | 1:18 | 9 | 20 | N | 0.2/0.4 | - Print in orientation given in STL - Allow to cool to room temperature before removing from print bed
Reciever_Lid.stl | 1 | 2:12 | 20 | 20 | N | 0.2/0.4 | - Print in orientation given in STL
Reciever_Base.stl | 1 | 5:47 | 44 | 20 | N | 0.2/0.4 | - Print in orientation given in STL
Transmitter_Button.stl | 2 | 0:02 | 0.2 | 20 | N | 0.2/0.4 | - Print in orientation given in STL
Transmitter_Cover.stl | 2 | 0:09 | 0.5 | 20 | N | 0.2/0.4 | - Print in orientation given in STL - Trim any brim or elephants foot from bottom

# Customization Options

- Each different section of the device can be printed in any colour PLA.
- The Fusion files for the device are provided, so images and text can be added to the device.

# Post-Processing

- Use a hobby knife to remove any sharp edges, elephants foot, or stringing.

# Examples of Quality Prints

Photos of Transmitter_Lid.stl

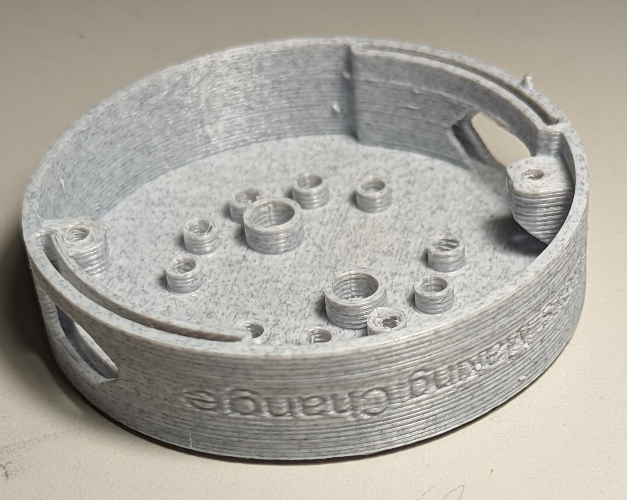
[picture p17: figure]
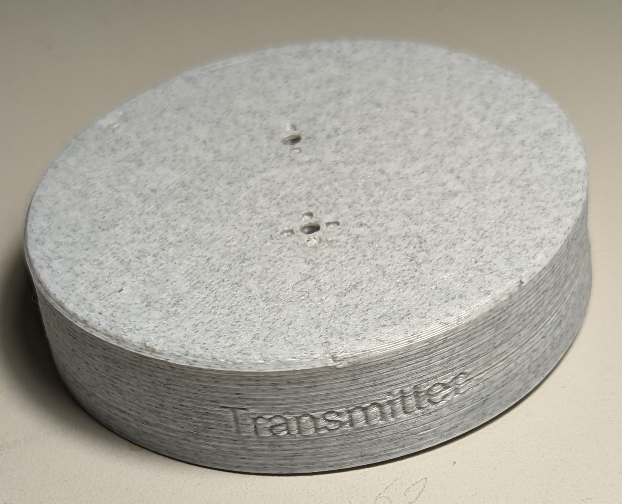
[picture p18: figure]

Photos of Transmitter_Base.stl

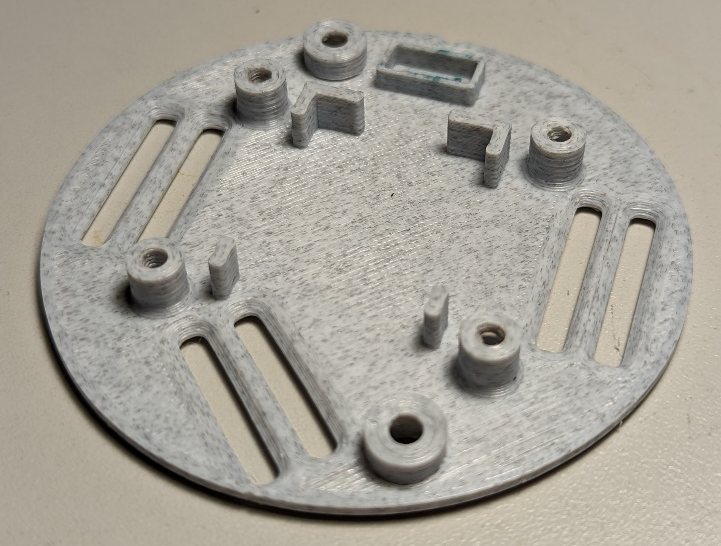
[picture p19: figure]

Photos of Receiver_Lid.stl

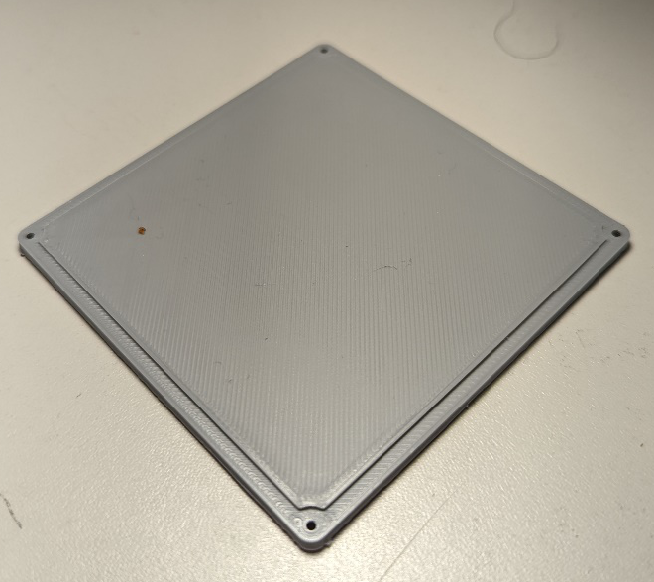
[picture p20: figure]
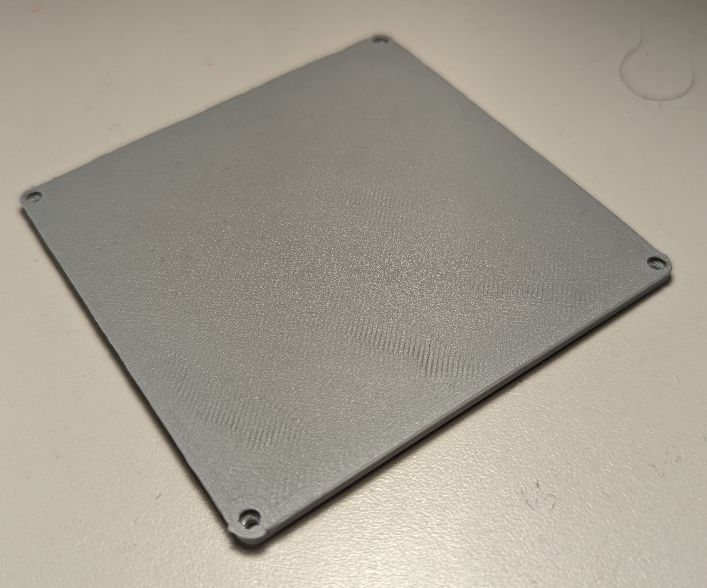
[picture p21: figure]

Photos of Receiver_Base.stl

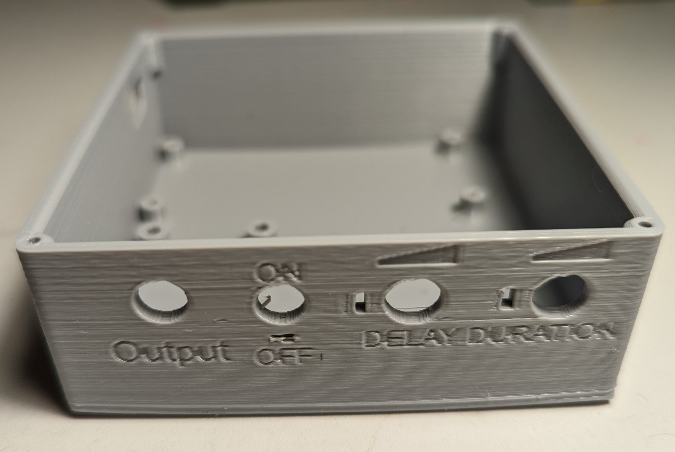
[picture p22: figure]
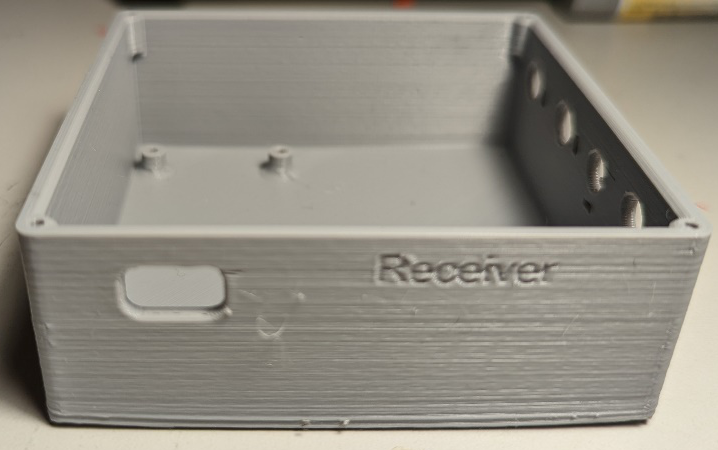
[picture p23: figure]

Photos of Transmitter_Cover.stl

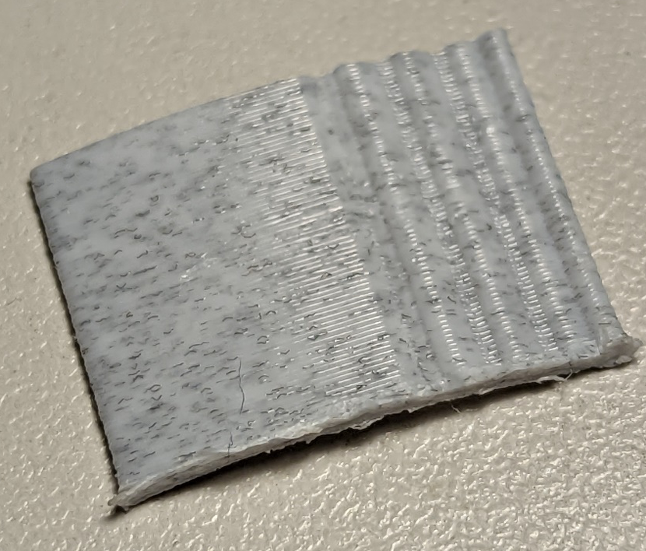
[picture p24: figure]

Photos of Transmitter_Button.stl

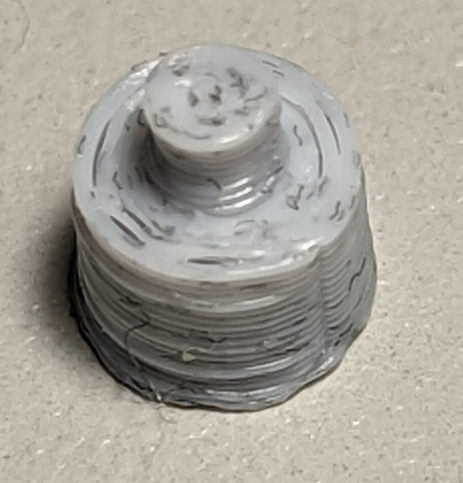
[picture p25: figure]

© 2022 by Neil Squire. This work is licensed under the CC BY SA 4.0 License: http://creativecommons.org/licenses/by-sa/4.0 Files available at https://makersmakingchange.com/project/wearable-clap-switch/ Page 2 of 3

V1.0 | December 2022 Wearable Clap Switch 3D Printing Guide

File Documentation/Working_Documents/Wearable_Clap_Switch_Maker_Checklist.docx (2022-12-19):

# Maker To Do List

- Read through the Assembly Guide to become familiar with required components, tools, supplies, safety gear, and overall assembly steps.
- Talk to User about customization options (e.g., colour, any special requests, etc.)
- Order hardware components
- Print all 3D printed parts
- Gather tools, supplies, and safety equipment.
- Assemble the device
- Test device
- Print “User Quick Guide”

# Items to Give to User

- Assembled, tested device
- “User Quick Guide”

© 2022 by Neil Squire. This work is licensed under the CC BY SA 4.0 License: http://creativecommons.org/licenses/by-sa/4.0 Files available at https://makersmakingchange.com/project/wearable-clap-switch/ Page 2 of 3

V1.0 | December 2022 Wearable Clap Switch Maker Checklist

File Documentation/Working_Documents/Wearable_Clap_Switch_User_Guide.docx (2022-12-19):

## Introduction

The Wearable Clap Switch is a hand mounted device that activates a switch operated device with a clap of the hands. The sensitivity of the clap detection, the duration of the activation, and the delay between activations can all be set by a secondary user.

## Features

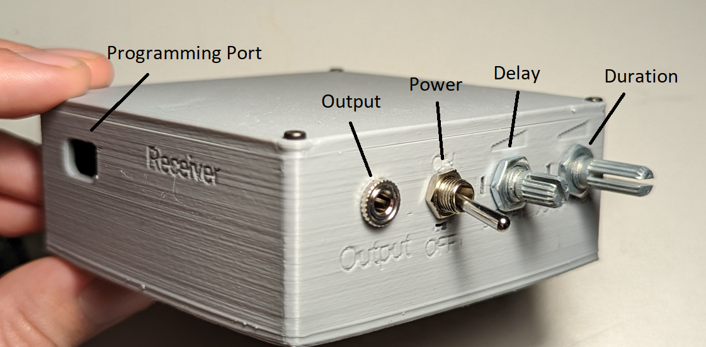
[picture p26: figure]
Labelled diagram of the receiver
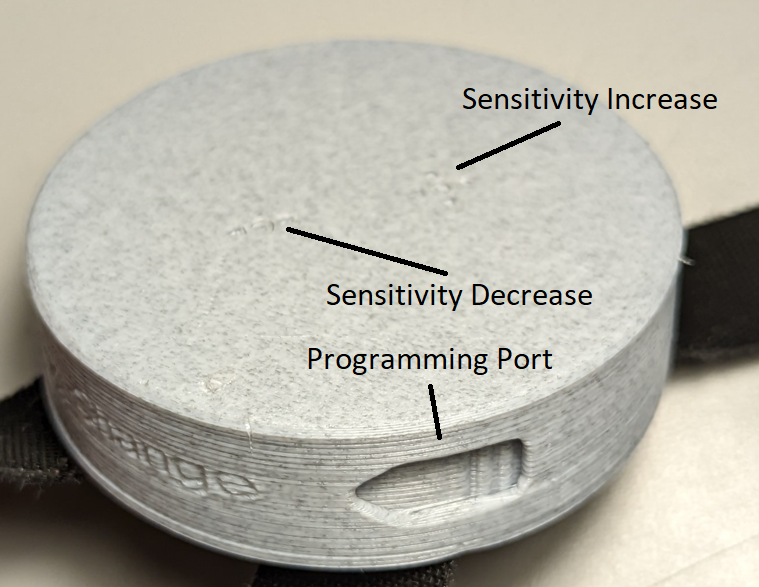
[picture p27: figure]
Labelled diagram of the back of the transmitter
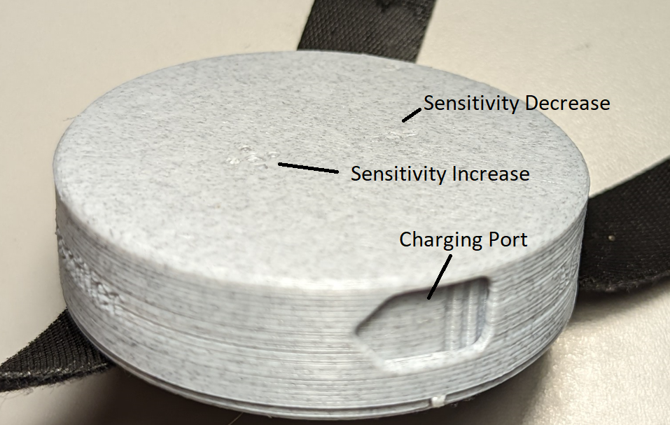
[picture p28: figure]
Labelled diagram of the front of the transmitter

## Usage

Transmitter

To activate the transmitter, slide the power switch on the bottom of the transmitter. The transmitter will start looking for a connection, and if a receiver is broadcasting, the two will connect. Once the two have connected, the transmitter will send a signal to the receiver whenever it detects a clap.

The sensitivity of the clap detection can be adjusted with the two buttons on the top of the case, as the sensitivity increases, the number of LEDs in the circle that are illuminated will increase, and the opposite will happen as the sensitivity decreases.

To charge the transmitter, open the port nearest the power switch, and use tweezers to unplug the JST connector and pull it out of the enclosure. It can then be plugged into the charging board, which connects to a Micro USB connector to charge the battery. The light on the charging board will go from red to green when the battery is fully charged.

Receiver

To active the receiver, flip the toggle switch from off to on. The receiver will start looking for a connection, and if the transmitter is broadcasting, the two will connect. Once they have connected, the receiver will power a relay to activate the mono jack.

To change how long the jack stays activated, adjust the potentiometer labeled Duration. To change the cooldown between activations, adjust the potentiometer labeled Delay.

To charge the receiver, plug a USB C connector into the port on the side of the case. The light on the inside will go from red to green when it is fully charged.

## Compatibility

The Wearable Clap Switch is compatible with any switch enabled device.

## Specifications

Transmitter

Weight: 45g

Dimensions: Diameter 70mm, height 20mm

Receiver

Weight: 119g

Dimensions: 85x85x35mm

## Cleaning

The device can be wiped clean with a damp cloth.

© 2022 by Neil Squire. This work is licensed under the CC BY SA 4.0 License: http://creativecommons.org/licenses/by-sa/4.0 Files available at https://makersmakingchange.com/project/wearable-clap-switch/ Page 2 of 3

V1.0 | December 2022 Wearable Clap Switch user Quick Guide

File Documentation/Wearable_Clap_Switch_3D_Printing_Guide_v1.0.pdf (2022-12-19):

V1.0 | December 2022

## Wearable Clap Switch

## 3D PRINTING GUIDE

© 2022 by Neil Squire. (https://neilsquire.ca/)
This work is licensed under the CC BY SA 4.0 License: http://creativecommons.org/licenses/by-sa/4.0
Files available at https://makersmakingchange.com/project/wearable-clap-switch/ (https://makersmakingchange.com/?post_type=project&p=20045&preview=true) | Page 1 of 4

### 3D Printing Summary

Metrics | *Configuration 1*
Total Print Time (hr:min) | 12:08
Total Number of Components | 8
Typical Total Mass (g) | 90
Typical Number of Print Setups | 5

### 3D Printing Settings

Print File Name | Qty | Total Print Time (hr:min) | Mass (g) | Infill (%) | Support(Y/N) | Layer Height/ Nozzle Diameter(mm) | Notes (orientation, special settings, etc.)
Transmitter_Lid.stl | 1 | 2:29 | 16 | 20 | N | 0.2/0.4 | -Print in orientation given in STL
Transmitter_Base.stl | 1 | 1:18 | 9 | 20 | N | 0.2/0.4 | -Print in orientation given in STL - Allow to cool to room temperature before removing from print bed
Reciever_Lid.stl | 1 | 2:12 | 20 | 20 | N | 0.2/0.4 | -Print in orientation given in STL
Reciever_Base.stl | 1 | 5:47 | 44 | 20 | N | 0.2/0.4 | -Print in orientation given in STL
Transmitter_Button.stl | 2 | 0:02 | 0.2 | 20 | N | 0.2/0.4 | -Print in orientation given in STL
Transmitter_Cover.stl | 2 | 0:09 | 0.5 | 20 | N | 0.2/0.4 | -Print in orientation given in STL - Trim any brim or elephants foot from bottom

## 3D PRINTING GUIDE

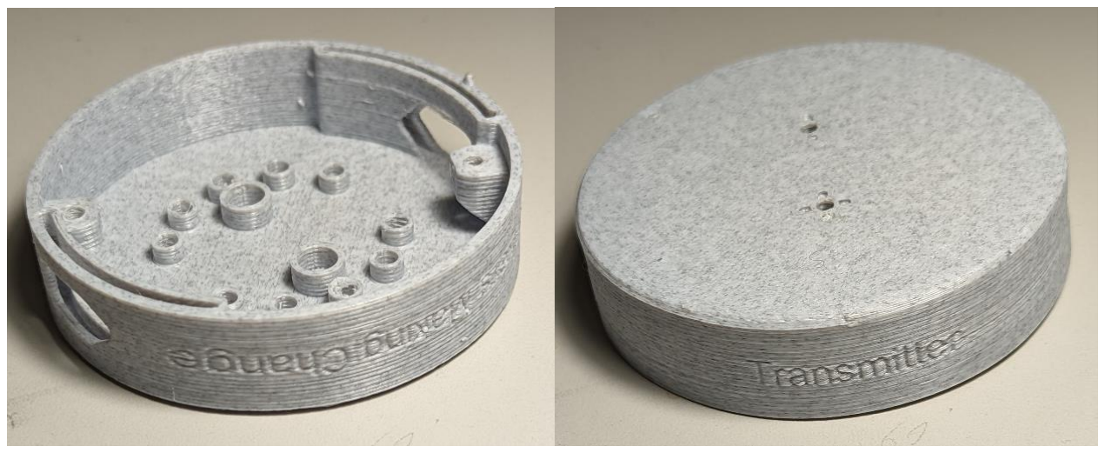
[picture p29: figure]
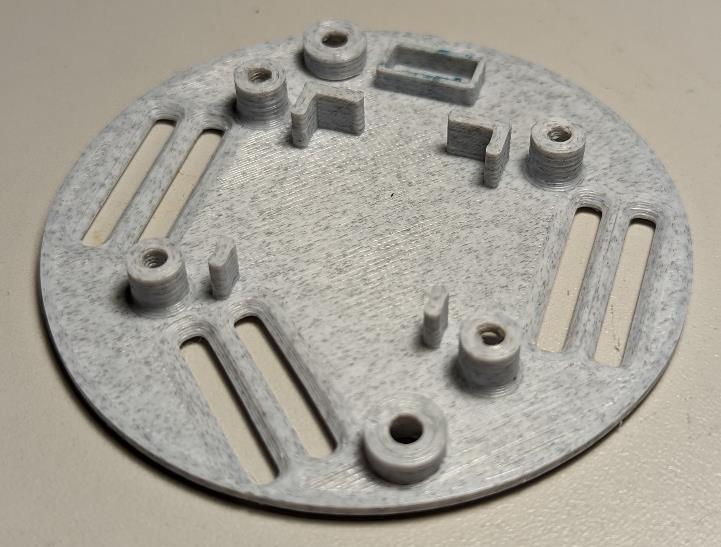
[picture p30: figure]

Files available at https://makersmakingchange.com/project/wearable-clap-switch/ (https://makersmakingchange.com/?post_type=project&p=20045&preview=true) | Page 2 of 4

### Customization Options

- If there are options for customization of the device include instructions here. This could be printing the device in multiple colors, custom markings, or any other way to customize the device.

### Post-Processing

- Add any processes that must be done after print such as removing supports

### Examples of Quality Prints

- Add photos of the prints below to show examples of what the component should look like after the print. This will help makers know if their print is good quality and if it is up to the expectations of the device.

Photos of Transmitter_Lid.stl

Photos of Transmitter_Base.stl

## 3D PRINTING GUIDE

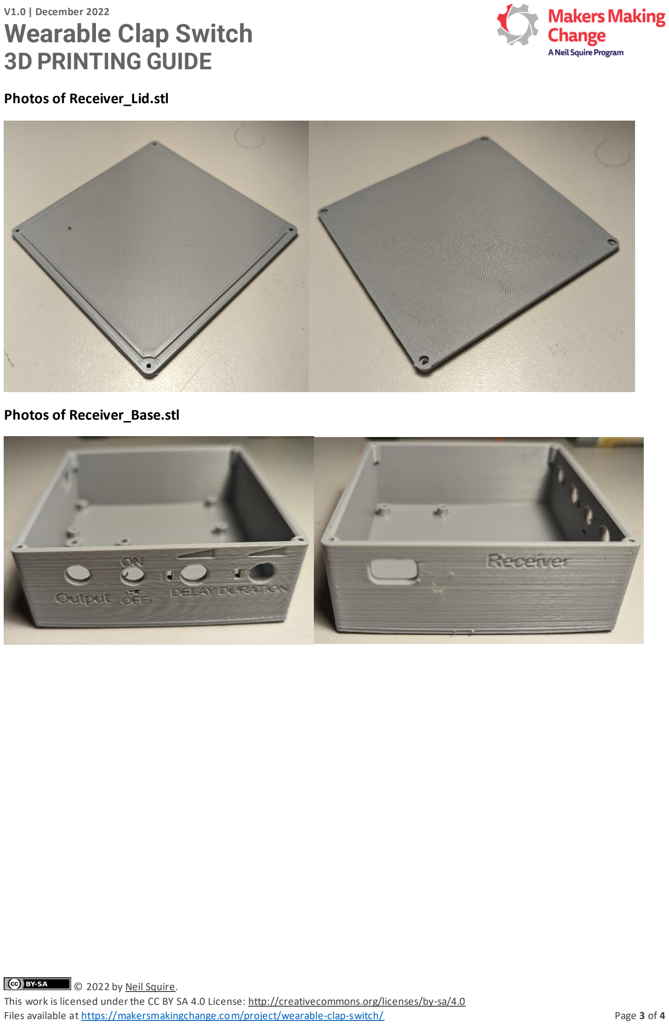
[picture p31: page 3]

Files available at https://makersmakingchange.com/project/wearable-clap-switch/ (https://makersmakingchange.com/?post_type=project&p=20045&preview=true) | Page 3 of 4

Photos of Receiver_Lid.stl

Photos of Receiver_Base.stl

## 3D PRINTING GUIDE

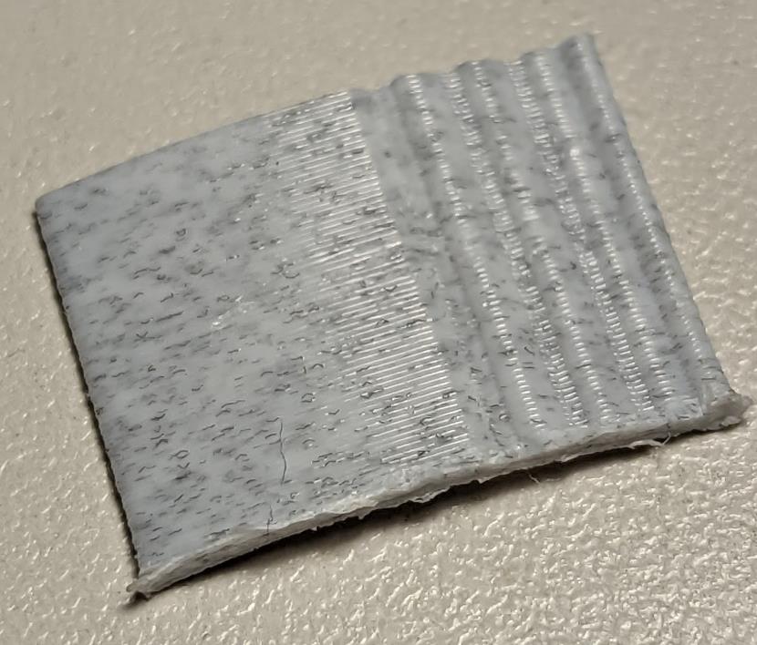
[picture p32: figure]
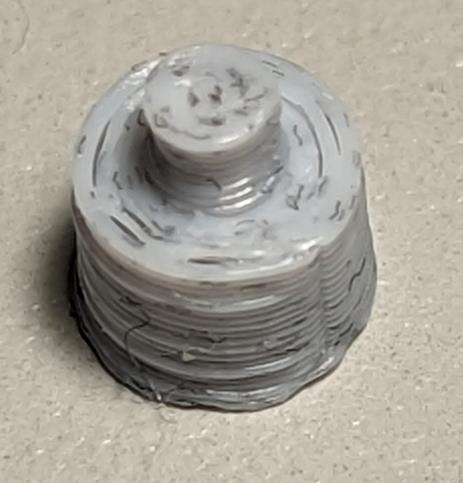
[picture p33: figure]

Files available at https://makersmakingchange.com/project/wearable-clap-switch/ (https://makersmakingchange.com/?post_type=project&p=20045&preview=true) | Page 4 of 4

Photos of Transmitter_Cover.stl

Photos of Transmitter_Button.stl

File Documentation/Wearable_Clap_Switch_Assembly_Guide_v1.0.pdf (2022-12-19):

V1.0 | December 2022

# Wearable Clap Switch

# ASSEMBLY GUIDE

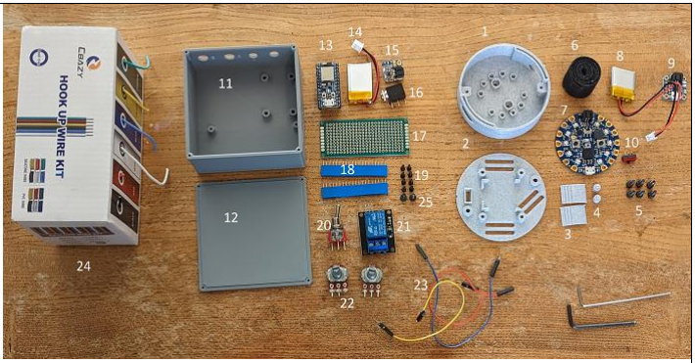
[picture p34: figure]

© 2022 by Neil Squire. (https://neilsquire.ca/)
This work is licensed under the CC BY SA 4.0 License: http://creativecommons.org/licenses/by-sa/4.0
Files available at https://makersmakingchange.com/project/wearable-clap-switch/ (https://makersmakingchange.com/?post_type=project&p=20045&preview=true) | Page 1 of 23

# Required Components

BOM 1. Transmitter Lid 2. Transmitter Base 3. Transmitter Cover x2 4. Transmitter Button x2 5. M3 screw x6 6. Double Sided Velcro 7. Circuit Playground Bluefruit 8. LiPo Battery 9. Battery Charger 10. Slide Switch 11. Receiver Base 12. Receiver Lid 13. ItsyBitsy nrf52408 14. LiPo Battery 15. Battery Backpack 16. 3.5mm mono jack 17. Protoboard

## 18. Female header pins 19. M2 Screw x8 20. Toggle switch 21. 5V relay 22. Potentiometer x2 23. Breadboard wire 24. Wire 25. M3 screw x2

# ASSEMBLY GUIDE

Files available at https://makersmakingchange.com/project/wearable-clap-switch/ (https://makersmakingchange.com/?post_type=project&p=20045&preview=true) | Page 2 of 23

# Required Tools

## - Soldering iron - Flush Cutters - Wire stripper - Solder - Electrical Tape - Screwdriver

# Required Personal Protective Equipment (PPE)

## - Safety Glasses

# ASSEMBLY GUIDE

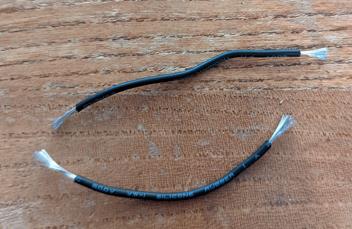
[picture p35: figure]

Files available at https://makersmakingchange.com/project/wearable-clap-switch/ (https://makersmakingchange.com/?post_type=project&p=20045&preview=true) | Page 3 of 23

# Assembly Instructions

## Transmitter

## Step 1

Take two 5cm pieces of wire and strip 1cm from each end.

# ASSEMBLY GUIDE

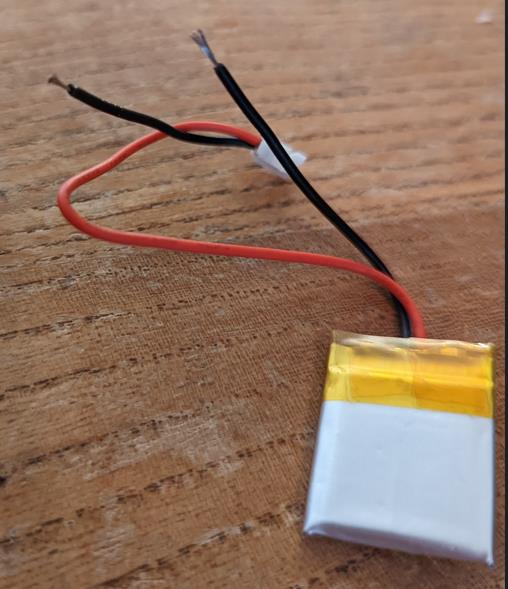
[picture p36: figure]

Files available at https://makersmakingchange.com/project/wearable-clap-switch/ (https://makersmakingchange.com/?post_type=project&p=20045&preview=true) | Page 4 of 23

## Step 2

Cut the black wire on the battery 4cm from the JST connector and strip 1cm on each end of the cut.

# ASSEMBLY GUIDE

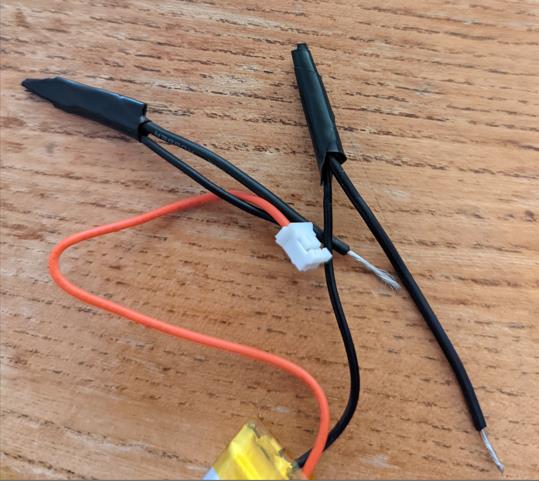
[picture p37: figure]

Files available at https://makersmakingchange.com/project/wearable-clap-switch/ (https://makersmakingchange.com/?post_type=project&p=20045&preview=true) | Page 5 of 23

## Step 3

## Solder the wires from step 1 onto each end of the stripped cut from step 2 and cover the

soldered joints with electrical tape.

# ASSEMBLY GUIDE

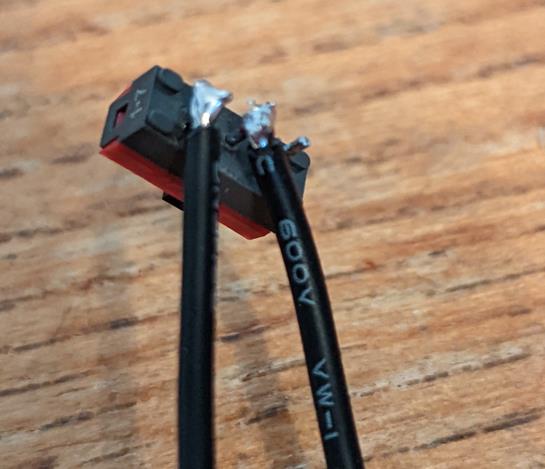
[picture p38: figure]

Files available at https://makersmakingchange.com/project/wearable-clap-switch/ (https://makersmakingchange.com/?post_type=project&p=20045&preview=true) | Page 6 of 23

## Step 4

Solder the remaining two ends of the wire to the middle and side terminal of the slide switch.

# ASSEMBLY GUIDE

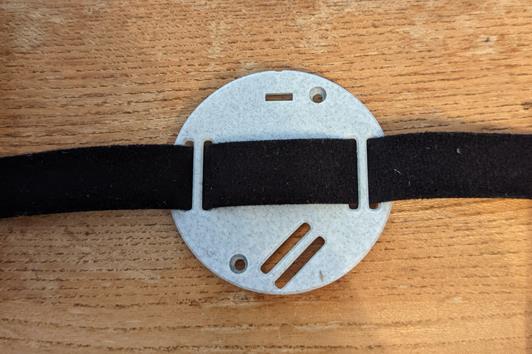
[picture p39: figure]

Files available at https://makersmakingchange.com/project/wearable-clap-switch/ (https://makersmakingchange.com/?post_type=project&p=20045&preview=true) | Page 7 of 23

## Step 5

Cut two lengths of double sided hook and loop fastener, roughly 10 and 8 inches long. Take the longer piece and weave it through the aligned slot in the base as shown in the picture, with the soft side facing away from the base.

# ASSEMBLY GUIDE

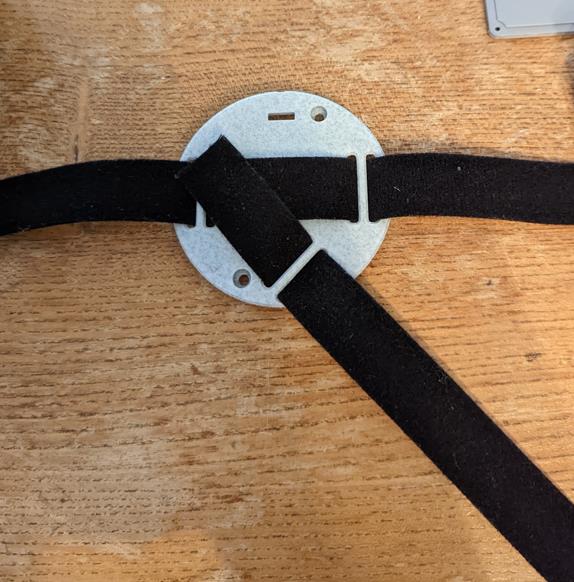
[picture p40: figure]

Files available at https://makersmakingchange.com/project/wearable-clap-switch/ (https://makersmakingchange.com/?post_type=project&p=20045&preview=true) | Page 8 of 23

## Step 6

Take the smaller piece of hook and loop fastener and weave it through the angled slot with the soft side facing away from the base. Align it as shown in the picture.

# ASSEMBLY GUIDE

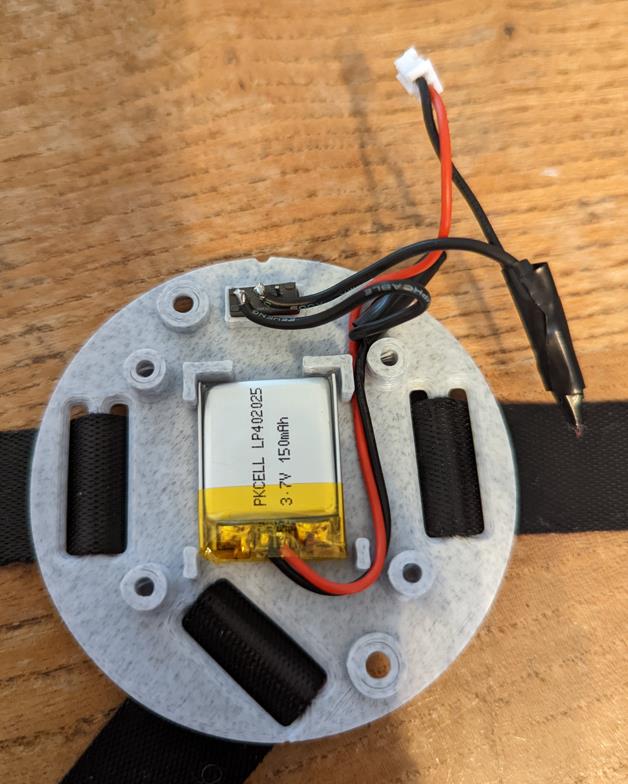
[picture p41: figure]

Files available at https://makersmakingchange.com/project/wearable-clap-switch/ (https://makersmakingchange.com/?post_type=project&p=20045&preview=true) | Page 9 of 23

## Step 7

Place the battery in the base and route the wires as shown in the picture. Secure the switch in the base with a dab of CA glue.

# ASSEMBLY GUIDE

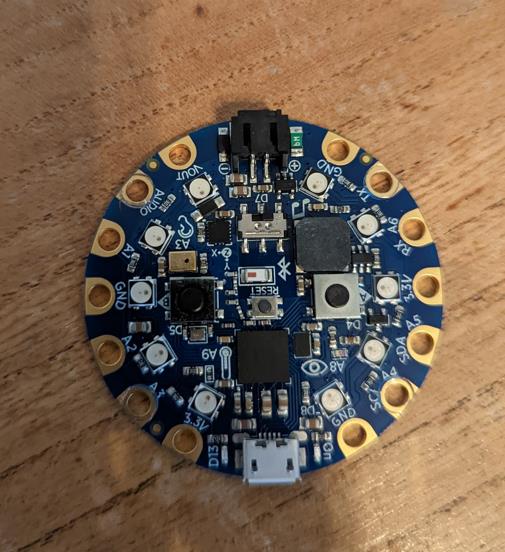
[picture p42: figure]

Files available at https://makersmakingchange.com/project/wearable-clap-switch/ (https://makersmakingchange.com/?post_type=project&p=20045&preview=true) | Page 10 of 23

## Step 8

Connect the Circuit Playground to the computer and upload the central_bleuartInstrucable0424.ino file to it.

# ASSEMBLY GUIDE

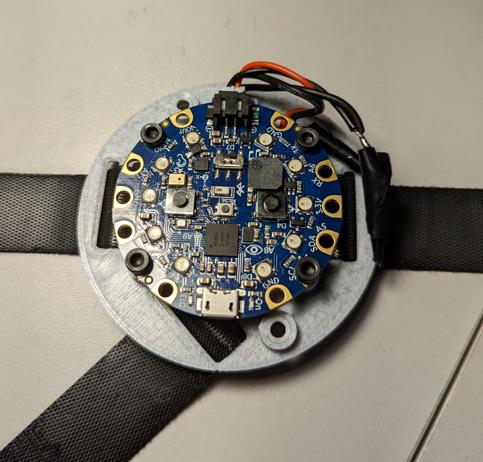
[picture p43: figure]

Files available at https://makersmakingchange.com/project/wearable-clap-switch/ (https://makersmakingchange.com/?post_type=project&p=20045&preview=true) | Page 11 of 23

## Step 9

Place the circuit playground on the four posts around the battery holder and use M3 screws to attach it onto each post.

# ASSEMBLY GUIDE

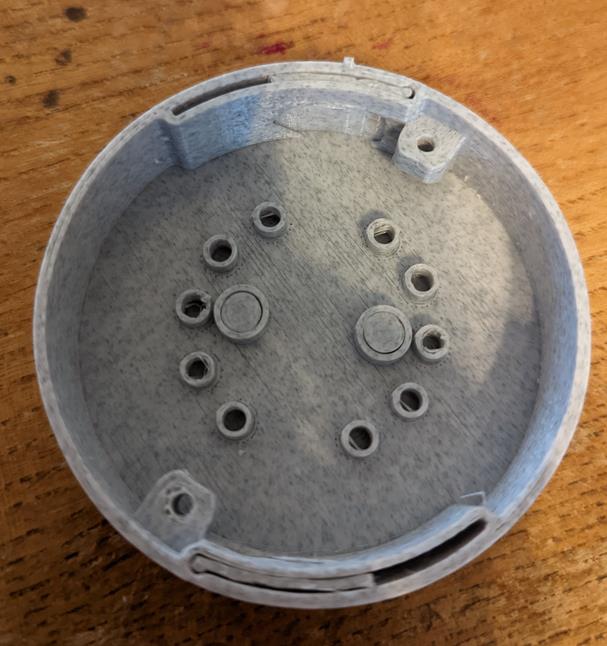
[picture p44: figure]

Files available at https://makersmakingchange.com/project/wearable-clap-switch/ (https://makersmakingchange.com/?post_type=project&p=20045&preview=true) | Page 12 of 23

## Step 10

Take the lid and place it upside down. Insert both covers into the slots by the ports, and both buttons in the holes in the centre.

# ASSEMBLY GUIDE

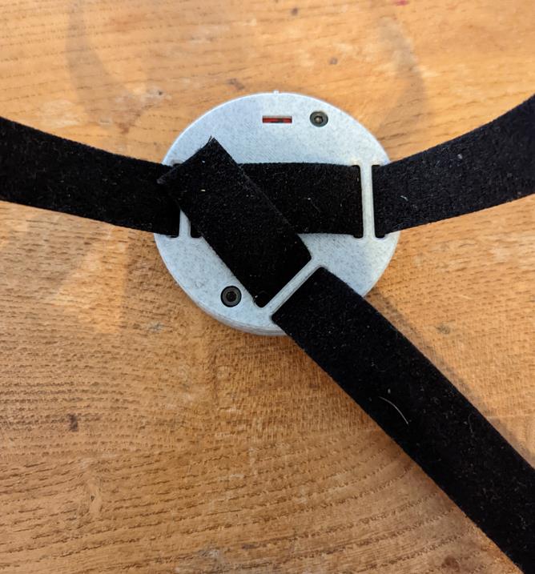
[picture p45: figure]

Files available at https://makersmakingchange.com/project/wearable-clap-switch/ (https://makersmakingchange.com/?post_type=project&p=20045&preview=true) | Page 13 of 23

## Step 11

Place the base assembly onto the lid, using the aligning peg to get the orientation correct. Secure the base onto the lid with two M3 screws.

# ASSEMBLY GUIDE

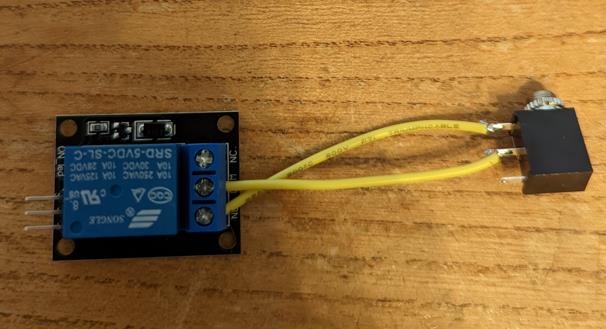
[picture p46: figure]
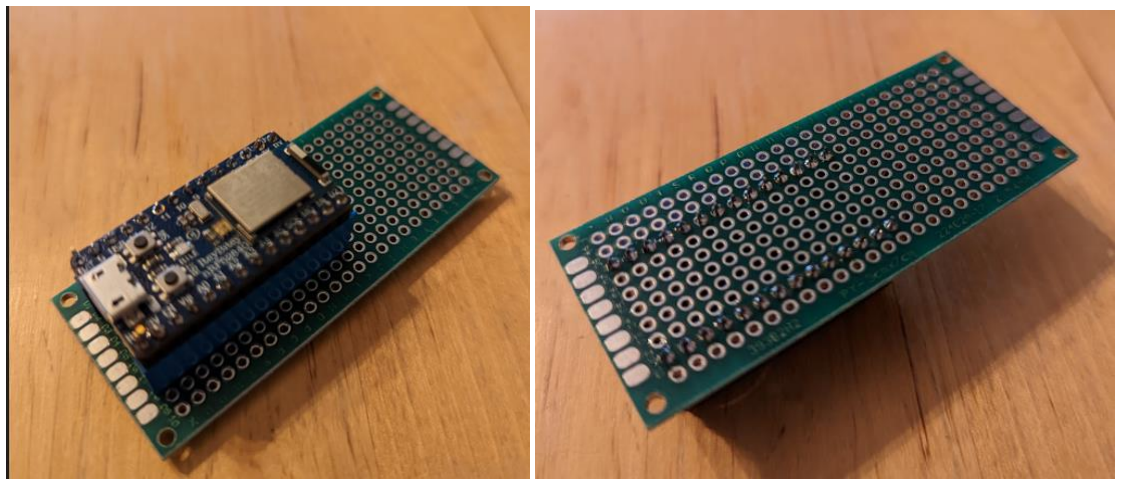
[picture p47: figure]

Files available at https://makersmakingchange.com/project/wearable-clap-switch/ (https://makersmakingchange.com/?post_type=project&p=20045&preview=true) | Page 14 of 23

## Receiver

## Step 1

Cut two 6cm pieces of wire and strip 1cm from each end. Solder one end of each wire to the 3.5mm mono jack as shown in the picture. Connect the other ends to the NO and COM terminals on the relay.

## Step 2

Cut 2 lengths of female headers to match the pins on the ItsyBitsy microcontroller. Attach the headers to the ItsyBitsy and place the headers onto the protoboard as shown in the picture. Solder the headers into place.

# ASSEMBLY GUIDE

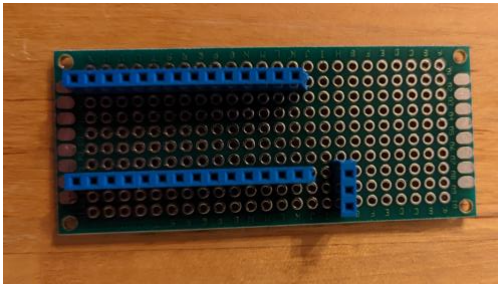
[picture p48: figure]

Files available at https://makersmakingchange.com/project/wearable-clap-switch/ (https://makersmakingchange.com/?post_type=project&p=20045&preview=true) | Page 15 of 23

## Step 3

Cut a 3 pin long section of female header and solder it to the protoboard as shown in the photo. Insert the battery backpack.

# ASSEMBLY GUIDE

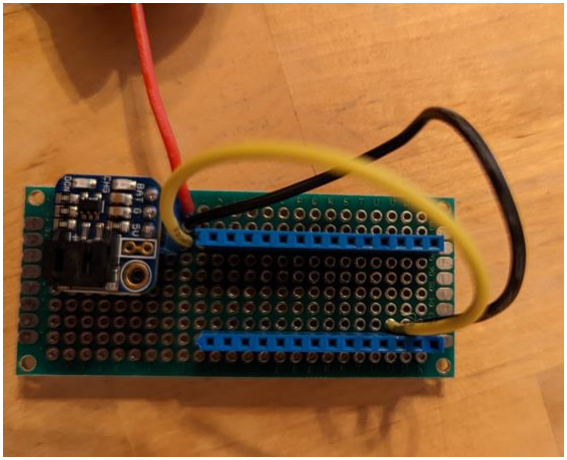
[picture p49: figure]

Files available at https://makersmakingchange.com/project/wearable-clap-switch/ (https://makersmakingchange.com/?post_type=project&p=20045&preview=true) | Page 16 of 23

## Step 4

Cut 4 10cm pieces of wire and strip 1cm from each end. Use two of these pieces to connect the 5V pin on the battery backpack header to the USB pin on the ItsyBitsy header, and the G pin on the battery

## backpack header to the G pin on the ItsyBitsy header

# ASSEMBLY GUIDE

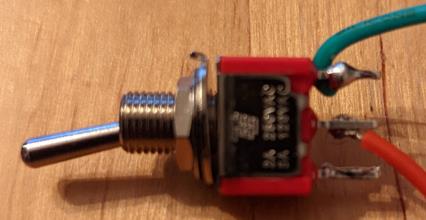
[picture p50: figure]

Files available at https://makersmakingchange.com/project/wearable-clap-switch/ (https://makersmakingchange.com/?post_type=project&p=20045&preview=true) | Page 17 of 23

## Step 5

Use the remaining two wires and solder them to the centre and right pin of the toggle switch. The right pin is the one alignment pin is on, see this picture [more here]. Solder the other two ends to connect the BAT pin on the battery pack header to the BAT pin on the ItsyBitsy header.

# ASSEMBLY GUIDE

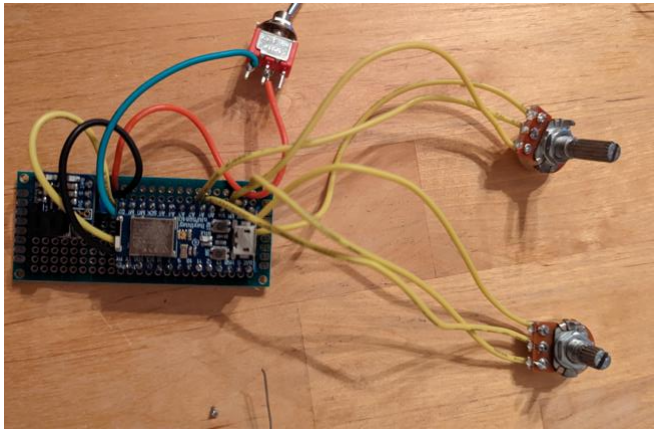
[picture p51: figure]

Files available at https://makersmakingchange.com/project/wearable-clap-switch/ (https://makersmakingchange.com/?post_type=project&p=20045&preview=true) | Page 18 of 23

## Step 6

Cut 6 15cm pieces of wire and solder the end of each to every pin on the two potentiometers as in the attached photo. Take the right wires on both potentiometers and connect them to the G pin on the ItsyBitsy header, and both left wires to the 3V pin on the ItsyBitsy header. Connect the middle wire on one potentiometer to the A1 pin on the ItsyBitsy header, and the other to the A2 pin.

# ASSEMBLY GUIDE

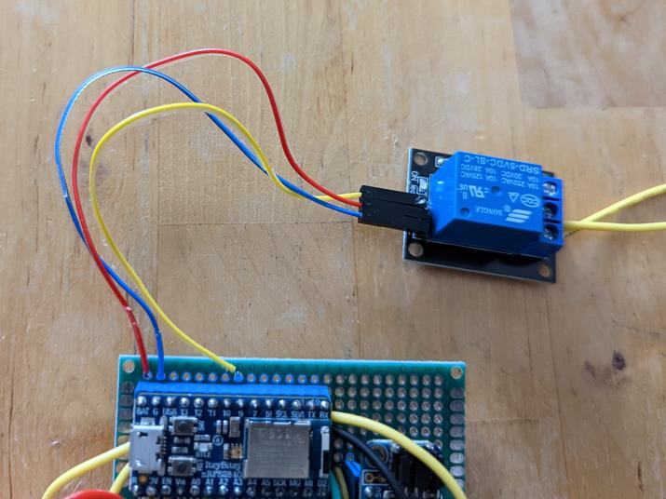
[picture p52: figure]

Files available at https://makersmakingchange.com/project/wearable-clap-switch/ (https://makersmakingchange.com/?post_type=project&p=20045&preview=true) | Page 19 of 23

## Step 7

Using breadboard wire, connect the – pin of the relay to the G pin of the ItsyBitsy header, the + pin to the battery pin, and the S pin to the 9 pin.

# ASSEMBLY GUIDE

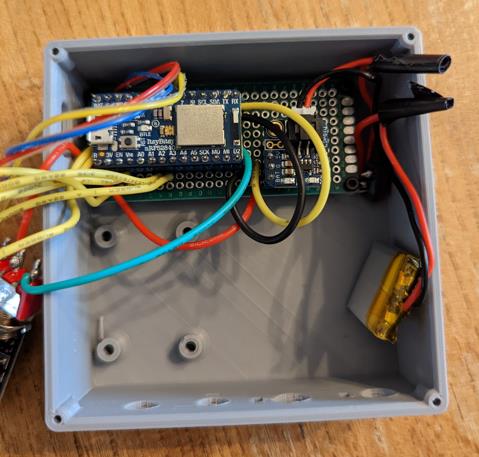
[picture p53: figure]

Files available at https://makersmakingchange.com/project/wearable-clap-switch/ (https://makersmakingchange.com/?post_type=project&p=20045&preview=true) | Page 20 of 23

## Step 8

Plug the battery into the battery backpack and screw the protoboard into the base using 4 M2 screws in the orientation shown in the picture.

# ASSEMBLY GUIDE

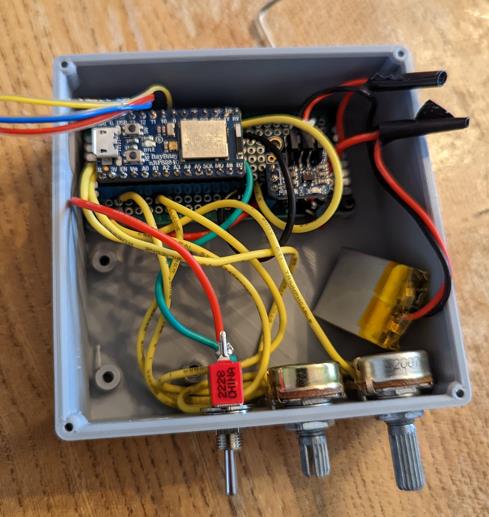
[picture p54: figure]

Files available at https://makersmakingchange.com/project/wearable-clap-switch/ (https://makersmakingchange.com/?post_type=project&p=20045&preview=true) | Page 21 of 23

## Step 9

Remove the retaining nuts on both potentiometers and the toggle switch. Insert the potentiometer connected to A2 through the hole labeled Duration, orienting it with the tab, and securing it in place with the retaining nut. Repeat this with the potentiometer connected to A1 and the Delay hole, and the toggle switch and the ON/OFF hole.

# ASSEMBLY GUIDE

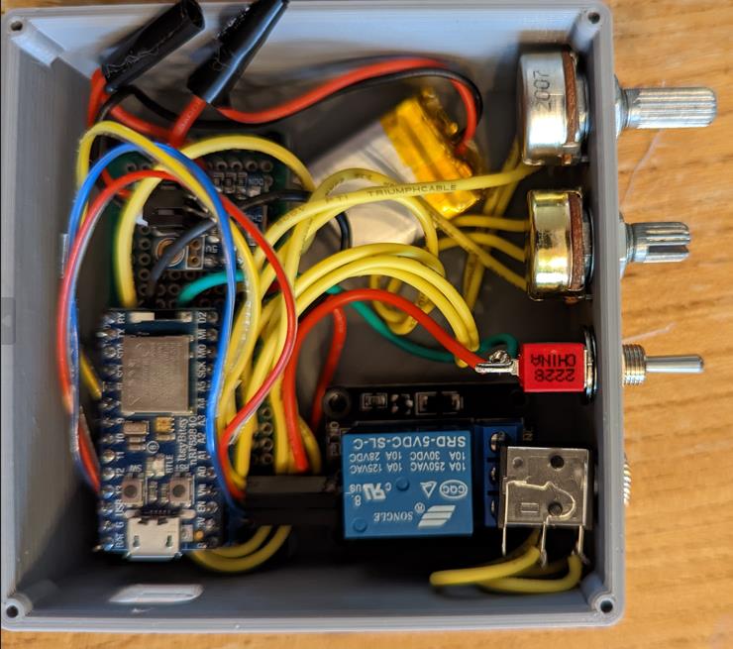
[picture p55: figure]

Files available at https://makersmakingchange.com/project/wearable-clap-switch/ (https://makersmakingchange.com/?post_type=project&p=20045&preview=true) | Page 22 of 23

## Step 10

Remove the retaining nut from the 3.5mm jack. Insert it through the last hole in the base, aligning the relay with the four posts on the base. Use two M3 screws on the rear posts to hold it in place. Secure the jack in place with the retaining nut.

# ASSEMBLY GUIDE

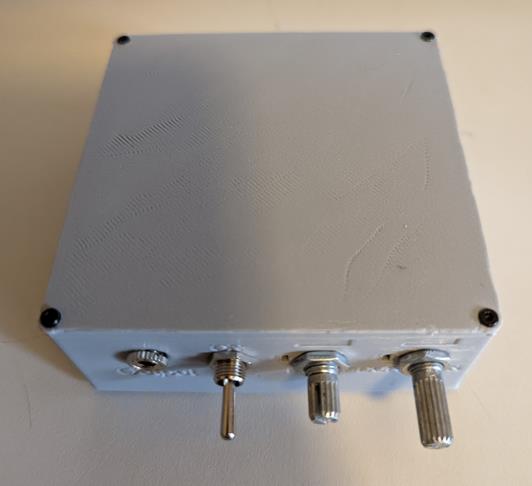
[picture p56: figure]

Files available at https://makersmakingchange.com/project/wearable-clap-switch/ (https://makersmakingchange.com/?post_type=project&p=20045&preview=true) | Page 23 of 23

## Step 11

Tuck the battery into the case and secure the lid with 4 M2 screws.

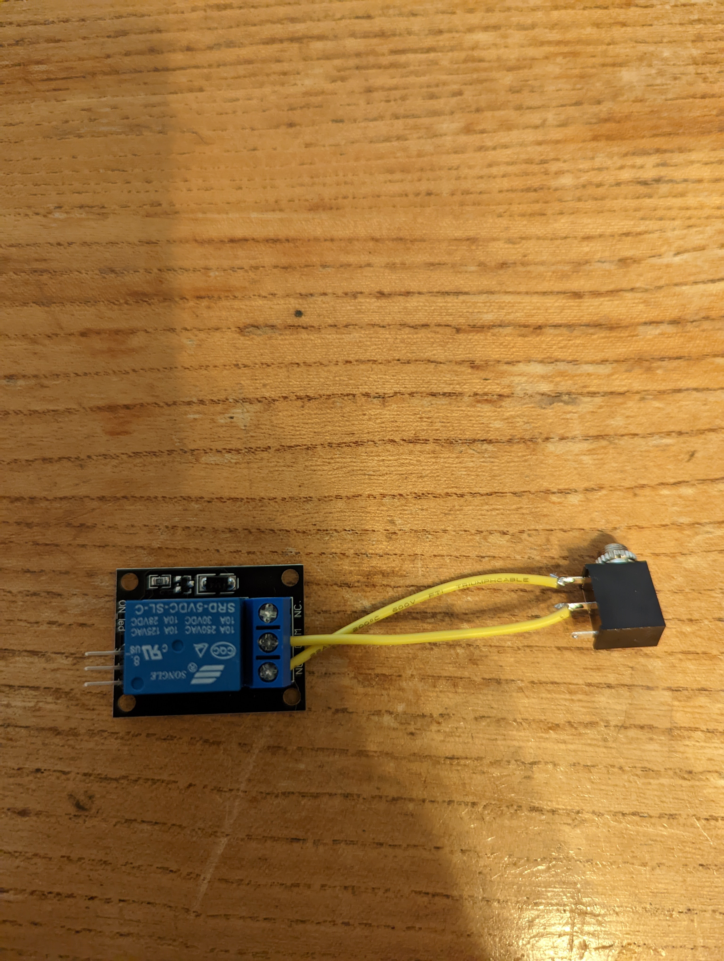
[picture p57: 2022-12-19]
Documentation/Working_Documents/Assembly_Photos/PXL_20221208_231523519.jpg

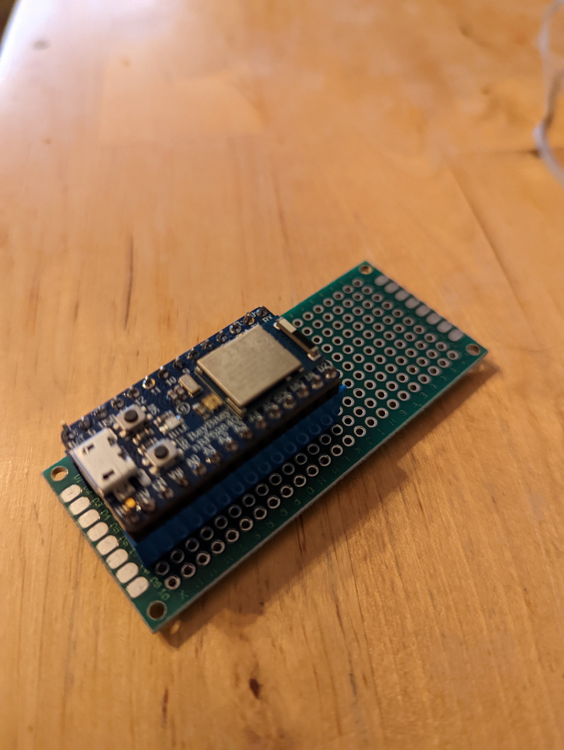
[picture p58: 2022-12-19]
Documentation/Working_Documents/Assembly_Photos/PXL_20221208_232138211.jpg

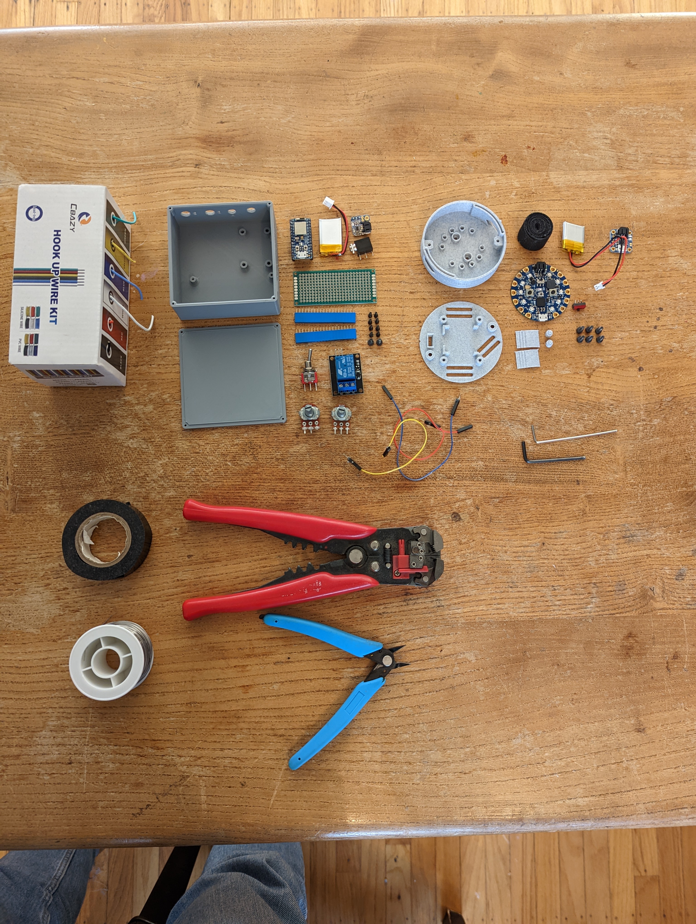
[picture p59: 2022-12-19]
Documentation/Working_Documents/Assembly_Photos/PXL_20221208_222818009.jpg

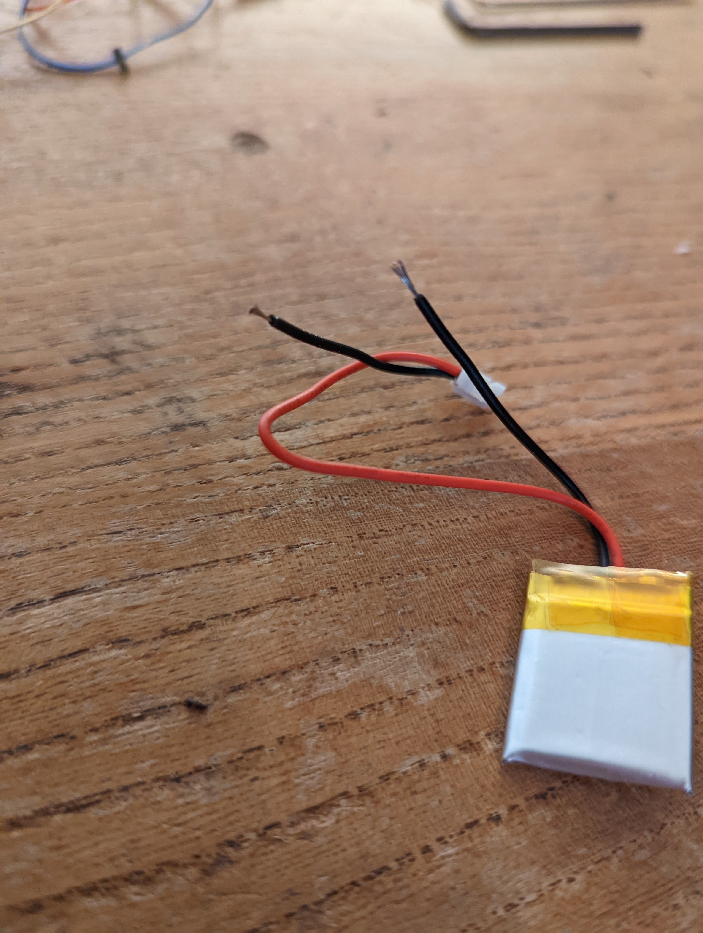
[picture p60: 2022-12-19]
Documentation/Working_Documents/Assembly_Photos/PXL_20221208_223511752.jpg

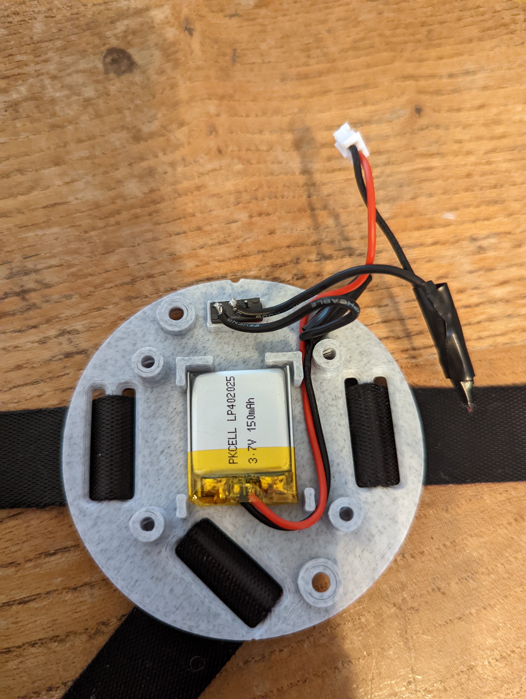
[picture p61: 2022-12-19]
Documentation/Working_Documents/Assembly_Photos/PXL_20221208_225142063.jpg

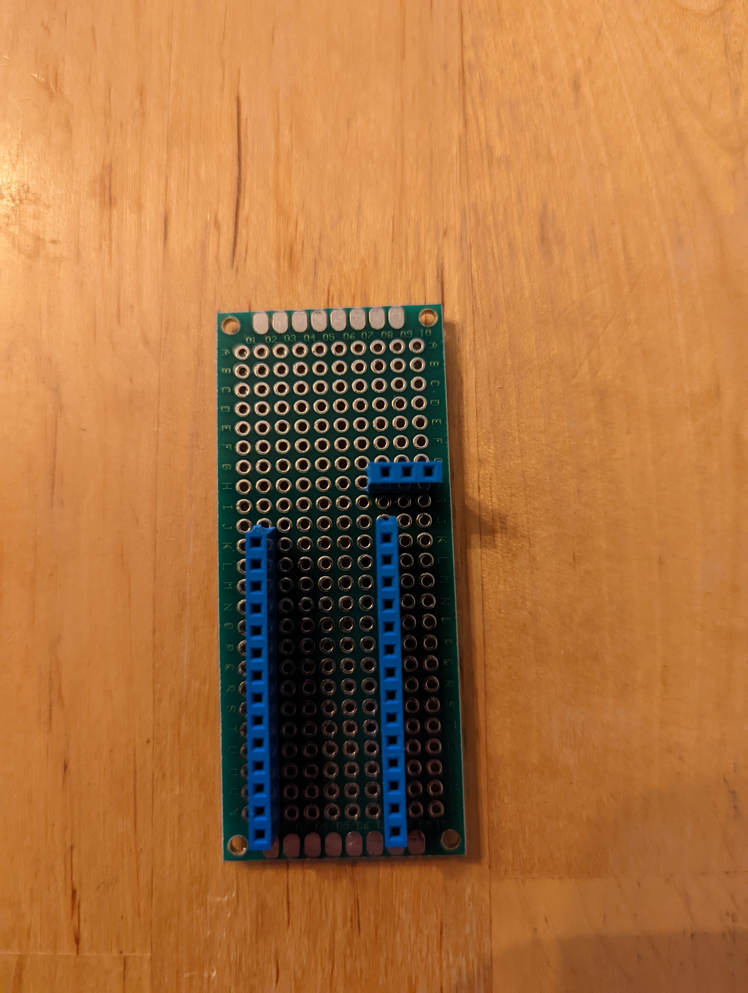
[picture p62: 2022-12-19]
Documentation/Working_Documents/Assembly_Photos/PXL_20221208_232415762.jpg

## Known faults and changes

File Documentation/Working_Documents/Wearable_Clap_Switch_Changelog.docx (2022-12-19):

# Version 1.0 | 2022/11/24

- Original design by r570sv (https://www.instructables.com/member/r570sv/) on instructables.com
- Improvements made to increase functionality
- Documentation by Neil Squire Society/ Makers Making Change

© 2022 by Neil Squire. This work is licensed under the CC BY SA 4.0 License: http://creativecommons.org/licenses/by-sa/4.0 Files available at https://makersmakingchange.com/project/wearable-clap-switch/ Page 2 of 3

V1.0 | December 2022 Wearable Clap Switch changelog

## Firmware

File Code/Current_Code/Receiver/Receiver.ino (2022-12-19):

/*********************************************************************
 This is an example for our nRF52 based Bluefruit LE modules

 Pick one up today in the adafruit shop!

 Adafruit invests time and resources providing this open source code,
 please support Adafruit and open-source hardware by purchasing
 products from Adafruit!

 MIT license, check LICENSE for more information
 All text above, and the splash screen below must be included in
 any redistribution
*********************************************************************/
#include <bluefruit.h>
#include <Adafruit_LittleFS.h>
#include <InternalFileSystem.h>
#define DELAY 15
#define DURATION 16
#define RELAY 9
// BLE Service
BLEDfu  bledfu;  // OTA DFU service
BLEDis  bledis;  // device information
BLEUart bleuart; // uart over ble
BLEBas  blebas;  // battery

int maxDelay = 5000; //milliseconds
int minDelay = 500; //milliseconds
int maxDuration= 5000; //milliseconds
int minDuration = 500; //milliseconds
int maxReading = 1023;//maximum possible reading 

void setup()
{
  Serial.begin(115200);//start serial
  pinMode(RELAY, OUTPUT);//setup realy trigger pin
  pinMode(DURATION,INPUT);//setup duration potentiometer pin
  pinMode(DELAY,INPUT);//setup delay potentiometer pin
  digitalWrite(RELAY,LOW);//ensure that relay starts open/switch is not active

  //COnfigure and Start Bluefruit
  Bluefruit.autoConnLed(true);// Setup the BLE LED to be enabled on CONNECT
  Bluefruit.configPrphBandwidth(BANDWIDTH_MAX);// Config the peripheral connection with maximum bandwidth 
  Bluefruit.begin();// start bluefruit
  Bluefruit.setTxPower(4);// Check bluefruit.h for supported values
  Bluefruit.Periph.setConnectCallback(connect_callback);
  Bluefruit.Periph.setDisconnectCallback(disconnect_callback);
  bledfu.begin();
  
  // Configure and Start Device Information Service
  bledis.setManufacturer("Adafruit Industries");
  bledis.setModel("Bluefruit Feather52");
  bledis.begin();

  // Configure and Start BLE Uart Service
  bleuart.begin();

  // Start BLE Battery Service
  blebas.begin();
  blebas.write(100);

  // Set up and start advertising
  startAdv();

}

int getDelay(){
  int delayReading = analogRead(DELAY);
  Serial.println(delayReading);
  return map(delayReading, 0, maxReading, minDelay, maxDelay);//scale the delay to fit into the maxDelay range map (value, fromLow, fromHigh,toLow, toHigh)
}

int getDuration(){
  int durationReading = analogRead(DURATION);
  Serial.println(durationReading);
  return map(durationReading, 0, maxReading, minDuration, maxDuration);//scale the duration to fit into the maxDuration range map (value, fromLow, fromHigh,toLow, toHigh)
}

void startAdv(void)
{
  // Advertising packet
  Bluefruit.Advertising.addFlags(BLE_GAP_ADV_FLAGS_LE_ONLY_GENERAL_DISC_MODE);
  Bluefruit.Advertising.addTxPower();

  // Include bleuart 128-bit uuid
  Bluefruit.Advertising.addService(bleuart);

  // Secondary Scan Response packet (optional)
  // Since there is no room for 'Name' in Advertising packet
  Bluefruit.ScanResponse.addName();
  
  Bluefruit.Advertising.restartOnDisconnect(true);
  Bluefruit.Advertising.setInterval(32, 244);    // in unit of 0.625 ms
  Bluefruit.Advertising.setFastTimeout(30);      // number of seconds in fast mode
  Bluefruit.Advertising.start(0);                // 0 = Don't stop advertising after n seconds  
}

void loop()
{
  // Forward from BLEUART to HW Serial
  while ( bleuart.available() )
  {
    //read character
    uint8_t ch;
    ch = (uint8_t) bleuart.read();
    //get delay and duration from input potentiometers
    int delayTime = getDelay();
    int durationTime =  getDuration();
    //display input, delay time, and duration time for debugging
    //Serial.write(ch);
    Serial.println(delayTime);
    Serial.println(durationTime);
    digitalWrite(RELAY,HIGH);//activate the switch
    delay(durationTime);//wait for the duration
    digitalWrite(RELAY,LOW);//deactivate the switch
    delay(delayTime);//wait for the delay
    //clear rest of buffer to prevent double triggering
    while ( bleuart.available() )
      {ch = (uint8_t) bleuart.read();
      }
      
    }
  }


// callback invoked when central connects
void connect_callback(uint16_t conn_handle)
{
  // Get the reference to current connection
  BLEConnection* connection = Bluefruit.Connection(conn_handle);

  char central_name[32] = { 0 };
  connection->getPeerName(central_name, sizeof(central_name));

  Serial.print("Connected to ");
  Serial.println(central_name);
}

/**
 * Callback invoked when a connection is dropped
 * @param conn_handle connection where this event happens
 * @param reason is a BLE_HCI_STATUS_CODE which can be found in ble_hci.h
 */
void disconnect_callback(uint16_t conn_handle, uint8_t reason)
{
  (void) conn_handle;
  (void) reason;

  Serial.println();
  Serial.print("Disconnected, reason = 0x"); Serial.println(reason, HEX);
}

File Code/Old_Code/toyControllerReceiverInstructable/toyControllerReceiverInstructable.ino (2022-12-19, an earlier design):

/*********************************************************************
  This is an example for our nRF52 based Bluefruit LE modules

  Pick one up today in the adafruit shop!

  Adafruit invests time and resources providing this open source code,
  please support Adafruit and open-source hardware by purchasing
  products from Adafruit!

  MIT license, check LICENSE for more information
  All text above, and the splash screen below must be included in
  any redistribution
*********************************************************************/

#include <bluefruit.h>

// OTA DFU service
BLEDfu bledfu;

// Uart over BLE service
BLEUart bleuart;

// Function prototypes for packetparser.cpp
uint8_t readPacket (BLEUart *ble_uart, uint16_t timeout);
float   parsefloat (uint8_t *buffer);
void    printHex   (const uint8_t * data, const uint32_t numBytes);
int motorRun, offTime, val;
// Packet buffer
extern uint8_t packetbuffer[];

void setup(void)
{
  Serial.begin(115200);
  // while ( !Serial ) delay(10);   // for nrf52840 with native usb
  pinMode(10, OUTPUT);
  pinMode(5, OUTPUT);
  digitalWrite(10, LOW);
  //pinMode(1, INPUT);
  //pinMode(2, INPUT);
  Serial.println(F("Adafruit Bluefruit52 Controller App Example"));
  Serial.println(F("-------------------------------------------"));

  Bluefruit.begin();
  Bluefruit.autoConnLed(true); //flash light
  Bluefruit.setTxPower(4);    // Check bluefruit.h for supported values
  Bluefruit.setName("Bluefruit52");

  // To be consistent OTA DFU should be added first if it exists
  bledfu.begin();

  // Configure and start the BLE Uart service
  bleuart.begin();

  // Set up and start advertising
  startAdv();

  Serial.println(F("Please use Adafruit Bluefruit LE app to connect in Controller mode"));
  Serial.println(F("Then activate/use the sensors, color picker, game controller, etc!"));
  Serial.println();
}

void startAdv(void)
{
  // Advertising packet
  Bluefruit.Advertising.addFlags(BLE_GAP_ADV_FLAGS_LE_ONLY_GENERAL_DISC_MODE);
  Bluefruit.Advertising.addTxPower();

  // Include the BLE UART (AKA 'NUS') 128-bit UUID
  Bluefruit.Advertising.addService(bleuart);

  // Secondary Scan Response packet (optional)
  // Since there is no room for 'Name' in Advertising packet
  Bluefruit.ScanResponse.addName();

  /* Start Advertising
     - Enable auto advertising if disconnected
     - Interval:  fast mode = 20 ms, slow mode = 152.5 ms
     - Timeout for fast mode is 30 seconds
     - Start(timeout) with timeout = 0 will advertise forever (until connected)

     For recommended advertising interval
     https://developer.apple.com/library/content/qa/qa1931/_index.html
  */
  Bluefruit.Advertising.restartOnDisconnect(true);
  Bluefruit.Advertising.setInterval(32, 244);    // in unit of 0.625 ms
  Bluefruit.Advertising.setFastTimeout(30);      // number of seconds in fast mode
  Bluefruit.Advertising.start(0);                // 0 = Don't stop advertising after n seconds
}

/**************************************************************************/
/*!
    @brief  Constantly poll for new command or response data
*/
/**************************************************************************/
void loop(void)
{
  digitalWrite(10, HIGH);
  // Wait for new data to arrive
  uint8_t len = readPacket(&bleuart, 1500);
  if (len == 0) {
    Serial.println(F("no message"));
    motorRun = analogRead(A1); // motor run
    offTime = analogRead(A2);
    /*
    Serial.print("MR    OT");
    Serial.println();
    Serial.print(motorRun);
    Serial.print("  ");
    Serial.print(offTime);
    Serial.println();
    */
    return;
  }
  Serial.println(F("Message Received!"));
  // Got a packet!
  printHex(packetbuffer, len);

  // Color
  if (packetbuffer[1] == 'C') {

    Serial.println(F("C Received! turn on toy"));
    motorRun = analogRead(A1); // motor run
    offTime = analogRead(A2);
    /*
    Serial.print("MR    OT");
    Serial.println();
    Serial.print(motorRun);
    Serial.print("  ");
    Serial.print(offTime);
    Serial.println();
*/
// we have to pulse on the toy, delay, then pulse off the toy
    digitalWrite(5, HIGH); // Turns on motor
    delay(400);  
    digitalWrite(5, LOW);
    val = map(motorRun, 0, 940, 1000, 6000);
    delay(val);            // waits based on mapped pot value
    digitalWrite(5, HIGH); // Turns on motor
    delay(400);
    digitalWrite(5, LOW);  // turn motor off
    val = map(offTime, 0, 940, 1000, 6000);
    digitalWrite(10, LOW);
    delay(val);            // get time to wait before we can run again
    digitalWrite(10, HIGH);
    readPacket(&bleuart, 1500); // flush buffer for any messages that may have came in behind the last one.
  }

  /*
    uint8_t red = packetbuffer[2];
    uint8_t green = packetbuffer[3];
    uint8_t blue = packetbuffer[4];
    Serial.print ("RGB #");
    if (red < 0x10) Serial.print("0");
    Serial.print(red, HEX);
    if (green < 0x10) Serial.print("0");
    Serial.print(green, HEX);
    if (blue < 0x10) Serial.print("0");
    Serial.println(blue, HEX);
    }

    // Buttons
    if (packetbuffer[1] == 'B') {
    uint8_t buttnum = packetbuffer[2] - '0';
    boolean pressed = packetbuffer[3] - '0';
    Serial.print ("Button "); Serial.print(buttnum);
    if (pressed) {
    Serial.println(" pressed");
    } else {
    Serial.println(" released");
    }
    }

    // GPS Location
    if (packetbuffer[1] == 'L') {
    float lat, lon, alt;
    lat = parsefloat(packetbuffer+2);
    lon = parsefloat(packetbuffer+6);
    alt = parsefloat(packetbuffer+10);
    Serial.print("GPS Location\t");
    Serial.print("Lat: "); Serial.print(lat, 4); // 4 digits of precision!
    Serial.print('\t');
    Serial.print("Lon: "); Serial.print(lon, 4); // 4 digits of precision!
    Serial.print('\t');
    Serial.print(alt, 4); Serial.println(" meters");
    }

    // Accelerometer
    if (packetbuffer[1] == 'A') {
    float x, y, z;
    x = parsefloat(packetbuffer+2);
    y = parsefloat(packetbuffer+6);
    z = parsefloat(packetbuffer+10);
    Serial.print("Accel\t");
    Serial.print(x); Serial.print('\t');
    Serial.print(y); Serial.print('\t');
    Serial.print(z); Serial.println();
    }

    // Magnetometer
    if (packetbuffer[1] == 'M') {
    float x, y, z;
    x = parsefloat(packetbuffer+2);
    y = parsefloat(packetbuffer+6);
    z = parsefloat(packetbuffer+10);
    Serial.print("Mag\t");
    Serial.print(x); Serial.print('\t');
    Serial.print(y); Serial.print('\t');
    Serial.print(z); Serial.println();
    }

    // Gyroscope
    if (packetbuffer[1] == 'G') {
    float x, y, z;
    x = parsefloat(packetbuffer+2);
    y = parsefloat(packetbuffer+6);
    z = parsefloat(packetbuffer+10);
    Serial.print("Gyro\t");
    Serial.print(x); Serial.print('\t');
    Serial.print(y); Serial.print('\t');
    Serial.print(z); Serial.println();
    }

    // Quaternions
    if (packetbuffer[1] == 'Q') {
    float x, y, z, w;
    x = parsefloat(packetbuffer+2);
    y = parsefloat(packetbuffer+6);
    z = parsefloat(packetbuffer+10);
    w = parsefloat(packetbuffer+14);
    Serial.print("Quat\t");
    Serial.print(x); Serial.print('\t');
    Serial.print(y); Serial.print('\t');
    Serial.print(z); Serial.print('\t');
    Serial.print(w); Serial.println();
    }
  */
}
